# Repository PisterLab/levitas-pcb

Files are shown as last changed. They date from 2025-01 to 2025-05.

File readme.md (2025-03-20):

# LeviTAS PCB

This is a PCB test platform originally built for the LeviTAS project.

A Raspberry Pi Pico microcontroller controls four 0-240V high voltage outputs and can simultaneously read from four FDC2112 capacitance sensors. The architecture and code should be straightforward to re-engineered to add more channels.

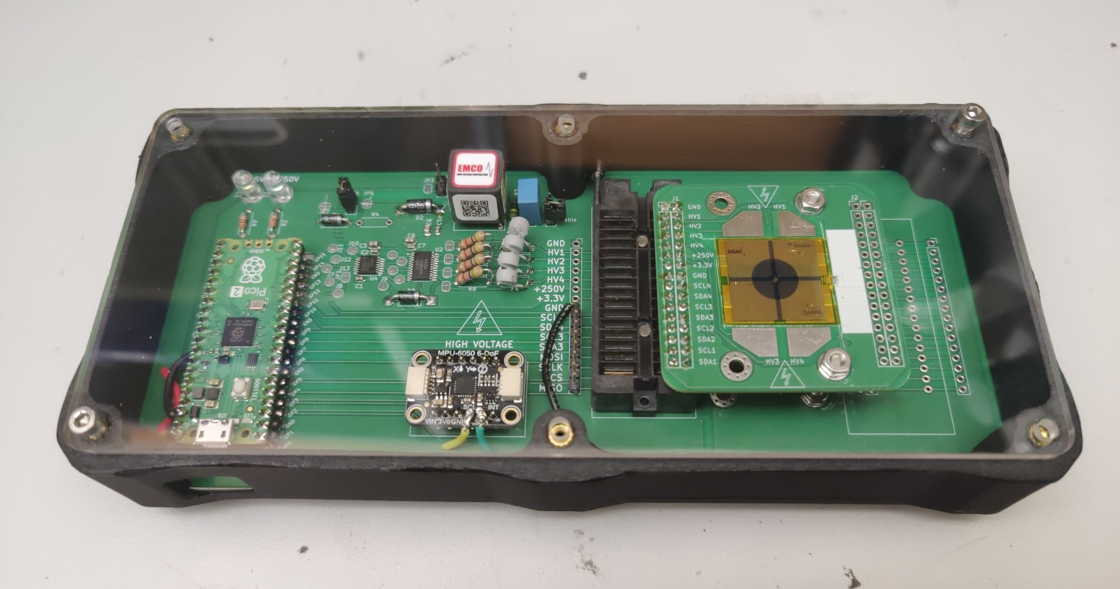
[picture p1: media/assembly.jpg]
Full assembled PCB and enclosure


# Programming / Firmware

This is how to program the microcontroller.

## Introduction

This project uses the Raspberry Pi RP2350 microcontroller, which is mounted to a Raspberry Pi Pico 2 dev board that we solder onto the main project PCB. The dev board is cheap and convenient because in addition to the RP2350 itself it includes flash memory, an oscillator, and power circuitry that we'd otherwise have to include anyway. The programming is the same either way.

The RP2350 is uniquely good for our use case because we need (a) four I2C buses running in parallel to read FDC2112 capacitance sensors, for which we use the PIO modules available only on the RP2040 and RP2350, and (b) we'd like floating-point math support built into the hardware, which the RP2350 has but the RP2040 does not. An FPGA might accomplish roughly the same tasks but is much more expensive and complicated to use.

Programming the RP2350 microcontroller is officially supported in C++ or MicroPython. We use C++ to more easily write programs that satisfy tight timing constraints (e.g., making a control loop as fast as possible). See the Documentation section below for links to the official documentation.

Note we're specifically using the 2.0.0 version of the SDK (because that's what we started with and haven't bothered to update it). Updating this requires updating the pico-sdk subfolder, every mention of the SDK version in other configuration files, and the version of the picotool utility used to upload the software. To minimize compilation issues, we also specifically chose to put the SDK files inside this git repo instead of requiring them to be downloaded to an external directory and linked.

## Installation and Running

Use the following steps to set up a software build environment for the Pico firmware on Linux or Windows, or follow the [official getting started guide](https://datasheets.raspberrypi.com/pico/getting-started-with-pico.pdf) for more generic instructions.

On Linux:
- Install gcc-arm-none-eabi compiler (arm-non-eabi-gcc on nixos)
- Install newlib
- Install cmake and gnumake
- Install picotool
- Install picotool udev rules
- In `firmware` folder, run `make build` to compile code and `make reload` to download and run (or `make` to do both).
- Use your favorite serial monitor to see data the Pico sends over USB.

On Windows:
- Install [Microsoft VS Code](https://code.visualstudio.com/) (This is preferable to VSCodium because the easiest way to read data from the Pico over USB is the Microsoft VS Code Serial Monitor extension, which doesn't work with VSCodium)
- Install the official [Raspberry Pi Pico Visual Studio Code extension](https://marketplace.visualstudio.com/items?itemName=raspberry-pi.raspberry-pi-pico)
- Open the `firmware` folder in VS Code. The Pi Pico extension should automatically detect this as a Pico project, and enable several commands under its quick access menu (click the extension icon on the Activity Bar, then under "Project" should be "Debug Project", "Compile Project", "Run Project (USB)", etc).
- Use the following commands:
  - "Compile Project" will compile (only) the software and put the compiled executables in a `build` subfolder, but note that "Configure CMake" must be run first.
  - "Configure CMake" will create a `build` subfolder and prepare the compilation based on configuration information in the `CMakeLists.txt` file. This is run automatically when the folder is opened in VS Code if recognized by the Pico extension. NOTE: THIS MUST BE MANUALLY RE-RUN EVERY TIME YOU CHANGE `CMakeLists.txt` FOR THE CHANGES TO BE APPLIED!
  - "Run Project (USB)" will load the program onto a Rasberry Pi Pico 2 board connected over USB (specifically, by running the `picotool` command line utility). If the Pico is in BOOTSEL mode (achieved by holding down the BOOTSEL button before plugging in USB) it will probably work immediately. If not, uploading can still work if USB communication was enabled on the already-running Pico program (which it is for this software, as per `CMakeLists.txt`), though you might need to press "Run Project (USB)" twice.
  - "Debug Project" and "Flash Project (SWD)" do not work without use of the Raspberry Pi Debug Probe (which we don't have).
- To see data the Pico is sending over USB, open the "SERIAL MONITOR" tab on the lower VS Code panel that also has "TERMINAL", "DEBUG CONSOLE", etc., set to 115200 baud and the correct COM port. Note this requires `pico_enable_stdio_usb(levitas 1)` to be set in `CMakeLists.txt` and `stdio_init_all();` to be called in `main.c` (which they are).

## Notable Firmware files

Inside the `firmware` folder:

- `CMakeLists.txt` configures compilation, and must be manually changed to include new source code files or other settings (e.g., importing a new sublibrary for the Pico SDK)
- `src/main.c` is the main source code file and holds the main LeviTAS control loop.
  - by default, this only prints capacitive sensor readings over USB; high voltage is set to zero
  - uncomment code in the main loop to enable high voltage output
- `src/pio_i2c.c`, `src/pio_i2c.h`, and `src/pio_i2c.pio` together form a library that can run I2C communication via the Pico PIOs. `src/main.c` uses this library to run four I2C ports in parallel (to connect to four FDC2112 chips).
- the following test code is unused but can be enabled by changing `CMakeLists.txt` to make them the main project file instead of `main.c`:
  - `src/test_fdc2112_i2c.c` tests only two of the four connected FDC2112 chips by using the two hardware built-in I2C modules (instead of PIO)
  - `src/test_fdc2112_pio_i2c.c` tests all four connected FDC2112 chips using the PIO library, and is almost identical to code in `src/main.c`.
  - `src/test_max5715_spi.c` tests the MAX5715 DAC and high voltage output, and is almost identical to code in `src/main.c`.
  - `src/test_mpu6050_i2c.c` displays data the MPU6050 accelerometer on the PCB motherboard using one of the hardware built-in I2C modules.

Other files:
- `Makefile` is used only for compiling on Linux, not for VS Code
- `.vscode` and `pico_sdk_import.cmake` are used only for VS Code with the official Pico VS Code extension, not on Linux
- the `build` subfolder is automatically generated by cmake when compiling and contains compiled executables in several formats, including UF2.

## Data Collection

The `data-collection/collect-data.py` and `data-collection/graph-data.py` Python programs in the `data-collection` subfolder of the main git repo can be used to automatically read the data the microcontroller sends over USB, then graph it. This provides much more useful data than manually looking at the printed output in a serial monitor.

## Some Useful Notes

There are several ways to upload code to a RP2040 or RP2350 chip:
1. Put into BOOTSEL mode (on Pi Pico dev board, hold down BOOTSEL buton when connecting power/USB), at which point the built-in ROM makes it act like a USB mass storage device. Upload file. (To verify file uploaded correctly, use picotool)
2. Put into BOOTSEL mode, use picotool to upload file
3. If USB communication enabled, can use picotool to force exit into BOOTSEL mode (use "picotool load -f" or "-F") then reboot (convenient!). There's no need to press the BOOTSEL button anymore. Note that sometimes this doesn't work on the first try, but repeating the process usually works.
4. Use SWD debugging interface.
Using the BOOTSEL mode (options 1,2) is necessary on a new chip, but afterward, as long as a program with USB communication enabled is running, option 3 is much more convenient. This is what we generally use.

Notes on the C/C++ SDK (from PDF manual):
- Consists of a large number of CMake libraries (in pico-sdk/src/rp2_common), which must be linked in the per-project CMakeLists.txt
  - The default library used in most examples is pico_stdlib, which includes several other libraries
  - the include files are typically in pico-sdk/src/rp2_common/(CMake library name)/include/(pico, hardware, gpio, etc)/(header.h)
- Apparently has some ability to build/debug running on the host operating system instead of the RP2040?
- Definitions for dev boards are in pico-sdk/src-boards/include/boards/
- The PDF manual has a bunch of examples
- Standard stdin/stdout can use (chapter 2.7):
  - UART (easy) (enabled by default) (disable by calling pico_enable_stdio_uart in CMakeLists.txt)
  - a USB CDC ACM virtual serial port (via TinyUSB) (enable by linking pico_stdio_usb or calling pico_enable_stdio_usb in CMakeLists.txt)
        (this is generally my preference?)
  - serial wire debug link (semihosting)
  - Segger RTT
- Can use bi_decl() in C code to store information in compiled binaries that picotool can access (e.g., comments, pin numbers)

## Documentation

There is a large amount of good official documentation at the following links. The most useful documentation is noted.

https://www.raspberrypi.com/documentation/microcontrollers/

RP2350 microcontroller:
- https://www.raspberrypi.com/products/rp2350/
- (good details on RP2350 hardware/capabilities) https://datasheets.raspberrypi.com/rp2350/rp2350-datasheet.pdf
- https://datasheets.raspberrypi.com/rp2350/hardware-design-with-rp2350.pdf
- https://datasheets.raspberrypi.com/rp2350/rp2350-product-brief.pdf

Pico and Pico 2 dev boards (which are almost identical):
- https://datasheets.raspberrypi.com/pico/pico-datasheet.pdf
- (good software getting-started guide) https://datasheets.raspberrypi.com/pico/getting-started-with-pico.pdf

Programming with C/C++:
- https://github.com/raspberrypi/pico-sdk
- (code examples) https://github.com/raspberrypi/pico-examples
- https://www.raspberrypi.com/documentation/microcontrollers/c_sdk.html
- https://www.raspberrypi.com/documentation/pico-sdk/index_doxygen.html
- (good software getting-started guide) https://datasheets.raspberrypi.com/pico/getting-started-with-pico.pdf
- (very thorough reference) https://datasheets.raspberrypi.com/pico/raspberry-pi-pico-c-sdk.pdf

Picotool:
- An official (and open source) CLI tool to work with compiled binaries and communicate with boards when in BOOTSEL mode (using the PICOBOOT interface; see RP2040 datasheet). Used to load and verify programs.
- https://github.com/raspberrypi/picotool

Raspberry Pi Debug Probe:
- Device to use UART or SWD debugging. Optional. We don't have one.
- https://www.raspberrypi.com/products/debug-probe/
- https://www.raspberrypi.com/documentation/microcontrollers/debug-probe.html

# More pictures

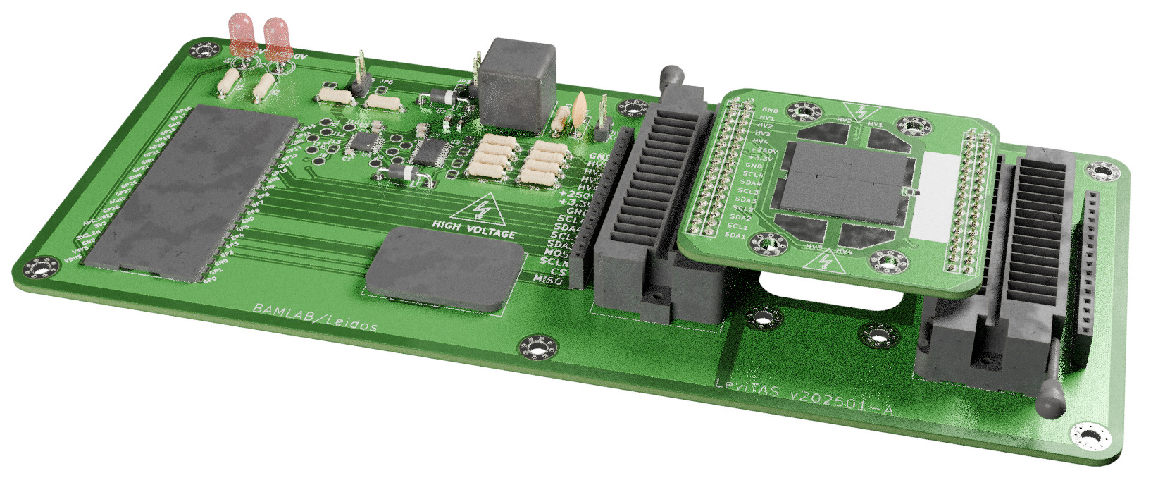
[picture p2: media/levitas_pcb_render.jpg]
Stacked PCBs

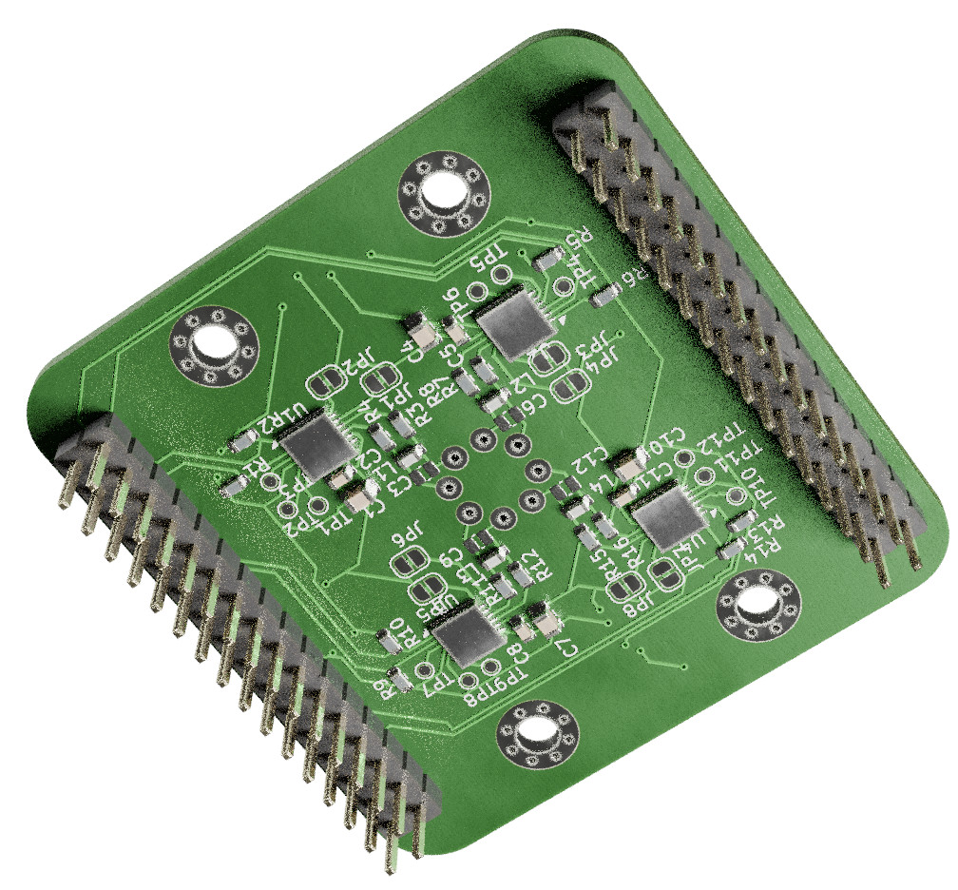
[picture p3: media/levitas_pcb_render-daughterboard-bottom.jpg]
Daughterboard


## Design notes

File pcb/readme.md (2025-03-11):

# Bill of Materials

MOTHERBOARD

|--------------------+-----------+-----------------------------------------+----------+--------------------------|
| TOTAL QTY TO ORDER | PER BOARD | part                                    | COST PER | DigiKey part             |
|--------------------+-----------+-----------------------------------------+----------+--------------------------|
|                  5 |         1 | RP2350 Pico 2 board (SC1631)            | $5       | 2648-SC1631CT-ND         |
|--------------------+-----------+-----------------------------------------+----------+--------------------------|
|                    |         2 | 220ohm R thru-hole                      |          | S220QCT-ND               |
|                    |         1 | LED 5mm thru-hole white                 |          | BL-BZX3V4V-1-B02-ND      |
|                    |         1 | LED 5mm thru-hole red                   |          | 754-WP7113SURCK-ND       |
|--------------------+-----------+-----------------------------------------+----------+--------------------------|
|                    |         4 | 100nF 0603 SMD caps                     |          | 311-1523-1-ND            |
|                    |         3 | 4.7uF 0805 SMD caps                     |          | 1276-1244-1-ND           |
|--------------------+-----------+-----------------------------------------+----------+--------------------------|
|                  5 |         1 | MAX5715AAUD+T DAC                       | $14.6    | 175-MAX5715AAUD+TCT-ND   |
|--------------------+-----------+-----------------------------------------+----------+--------------------------|
|                  5 |         1 | HV264 opamp                             | $7.8     | 150-HV264TS-GCT-ND       |
|                    |         1 | 1N4004 diode thru-hole                  |          | 4878-1N4004CT-ND         |
|--------------------+-----------+-----------------------------------------+----------+--------------------------|
|                    |         4 | 5kohm, thru-hole, 400V                  |          | CF12JT4K70CT-ND          |
|                 12 |         4 | PTC fuse PTCCL05H100SBE                 | $0.99    | BC3368-ND                |
|--------------------+-----------+-----------------------------------------+----------+--------------------------|
|                  0 |         1 | Q025-5C power supply                    |          | -                        |
|                  5 |         1 | TVS diode P6KE6.8A-E3/54                | $0.32    | P6KE6.8A-E3/54GICT-ND    |
|                 10 |         1 | 1Mohm, thru-hole, 400V                  | $0.03    | RNV14FAL1M00             |
|                    |         1 | 10nF, thru-hole, 400V                   |          | 495-75587-1-ND           |
|--------------------+-----------+-----------------------------------------+----------+--------------------------|
|                  3 |         1 | Stemma MPU-6050 accelerometer breakout  | $12.95   | 1528-3886-ND             |
|--------------------+-----------+-----------------------------------------+----------+--------------------------|
|                  6 |         2 | ZIF socket                              | $24.49   | A305-ND                  |
|                    |        10 | jumpers                                 |          |                          |
|                    |         3 | 20x breakaway male header pins          |          | 2057-PH1-20-UA-ND        |
|                    |         3 | 20x female header pins                  |          | S7053-ND                 |
|--------------------+-----------+-----------------------------------------+----------+--------------------------|
|                    |         1 | solder paste?                           |          | 315-NC191AX35T5-ND       |
|                    |         1 | rubber feet?                            |          | 3M156065-ND              |
|--------------------+-----------+-----------------------------------------+----------+--------------------------|
|                    |         8 | 100nF 0603 SMD caps                     |          | 311-1523-1-ND            |
|                    |         8 | 4.7uF 0805 SMD caps                     |          | 1276-1244-1-ND           |
|--------------------+-----------+-----------------------------------------+----------+--------------------------|
|                 15 |         4 | cap sensor FDC2112QDNTRQ1               | $6.59    | 296-44560-1-ND           |
|                    |         8 | resistor SMD 4.7k 0603                  |          | 311-4.7KGRCT-ND          |
|                    |         8 | resistor SMD 470  0603                  |          | A129684CT-ND             |
|                    |         8 | resistor SMD 0  0603 (just in case)     |          | RMCF0603ZT0R00CT-ND      |
|                    |         4 | inductor SMD 18uH 0603 MLF1608C180KTA00 |          | 445-1028-1-ND            |
|                    |         4 | cap SMD 33pF 0603                       |          | 478-KGM15ACG1H330JTCT-ND |
|--------------------+-----------+-----------------------------------------+----------+--------------------------|

Generate PCB gerbers according to
https://www.pcbway.com/blog/help_center/Generate_Gerber_file_from_Kicad.html
- use copper, paste, silkscreen, mask, edge.cuts
- uncheck "use extended x2 format"
- drill file with "minimal header" and "suppress leading zeros"

When ordering:
- remove label option
- extra urgent

# Accelerometer

Attached for board leveling and reference data.

Using breakout board instead of individual chip because I don't trust my soldering for something that small.

Can use either Adafruit Stemma MPU-6050 breakout or Stemma ADXL345 breakout (same board size, slightly more expensive).

# Motherboard/daughterboard connection

We attach the sensor daughterboard with an IC ZIF socket (well, two sockets). We use this instead of standard 0.1" header pins and sockets because inserting or removing header pins takes significant force, which can significantly shake or warp the daughterboard and might break the fragile MEMS devices on top. Ultimately, of course, we want to build a levitation system capable of sustaining high external forces, but our initial prototypes may not immediately reach that goal. That said, the motherboard PCB has footprints such that it can be assembled with standard female header pins instead of ZIF sockets with no other change in functionality.

The specific ZIF sockets se use are 32-6554-11 "CONN IC DIP SOCKET ZIF 32POS GLD" or 32-6554-10 "CONN IC DIP SOCKET ZIF 32POS TIN" from Aries Electronics due to their relatively high availability and robust construction.

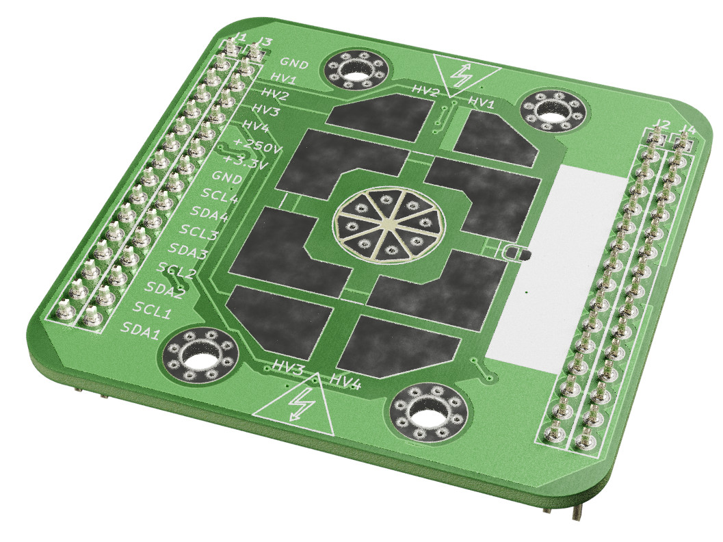
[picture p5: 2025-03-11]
media/levitas_pcb_render-daughterboard-front.jpg

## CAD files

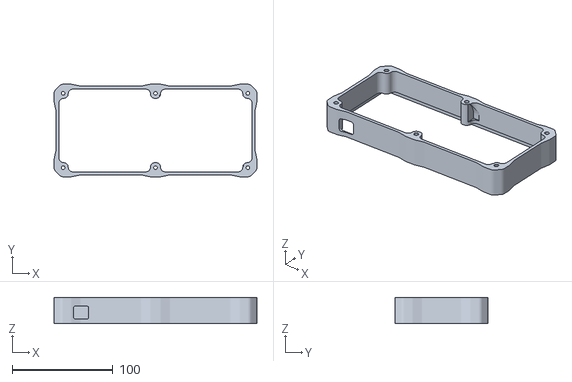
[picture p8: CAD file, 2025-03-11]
enclosure/levitas_pcb_assembly-case.STL
201.0 x 91.8 x 26.0

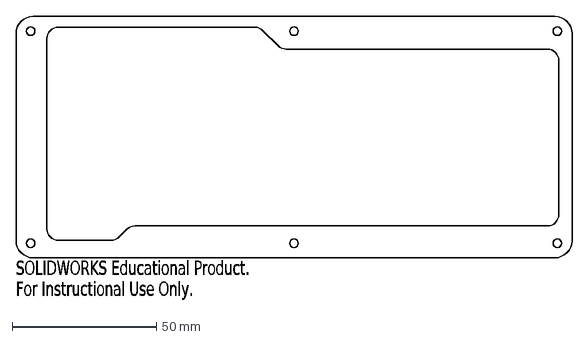
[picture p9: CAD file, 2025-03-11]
enclosure/case_pcb_cover_spacer.DXF
SOLIDWORKS Educational Product.
For Instructional Use Only.

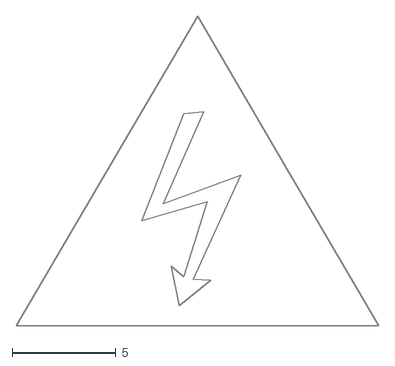
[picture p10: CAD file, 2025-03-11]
pcb/levitas-daughter.v2/high-voltage.dxf
17.5 x 14.9

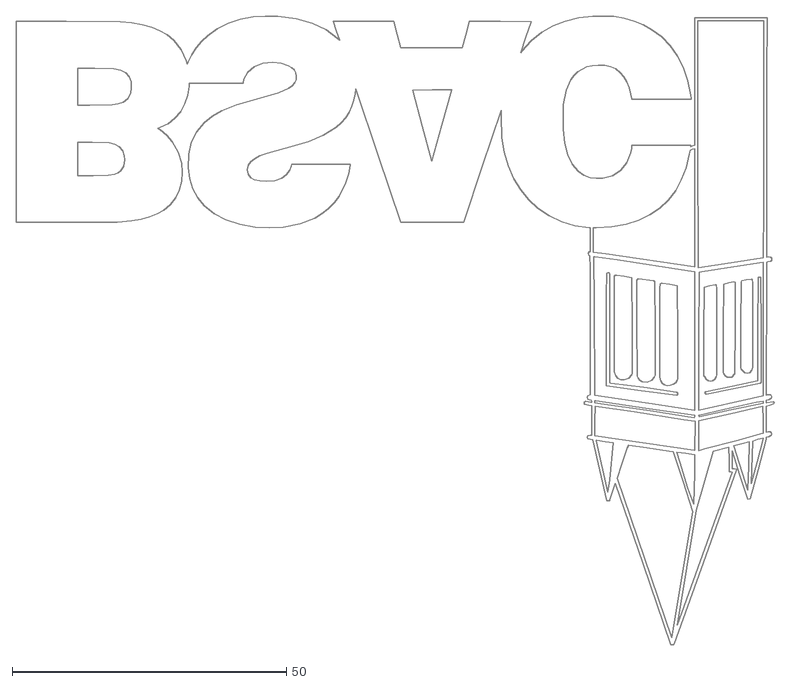
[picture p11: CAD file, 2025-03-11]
pcb/levitas/bsac_logo/BSAC-outline.dxf
138.3 x 114.7

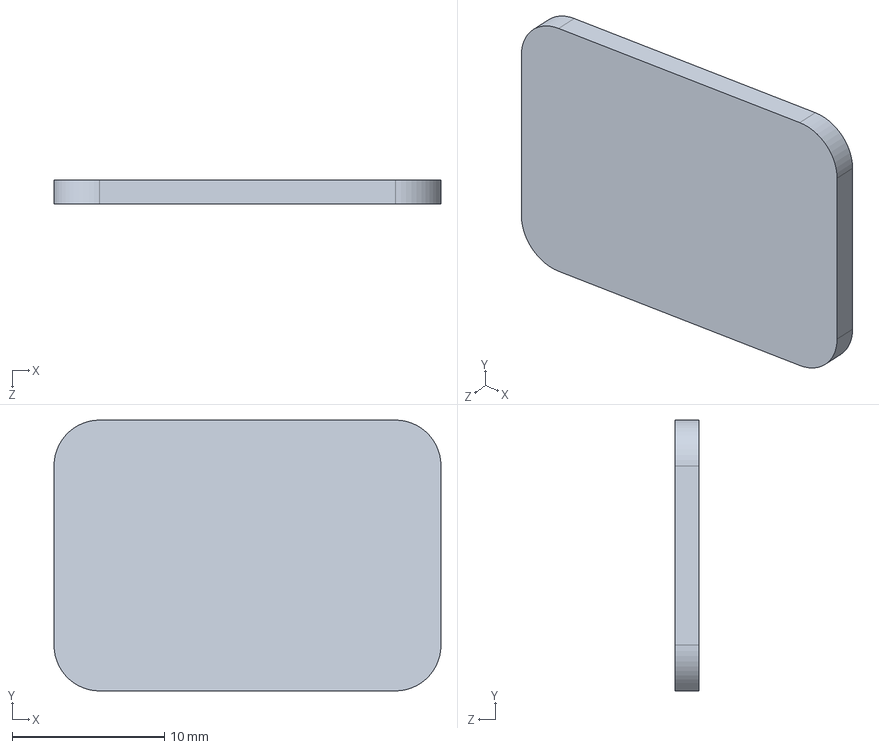
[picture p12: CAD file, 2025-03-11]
pcb/levitas/cad/stemma-mpu-6050.STEP
25.4 x 17.8 x 1.60 mm

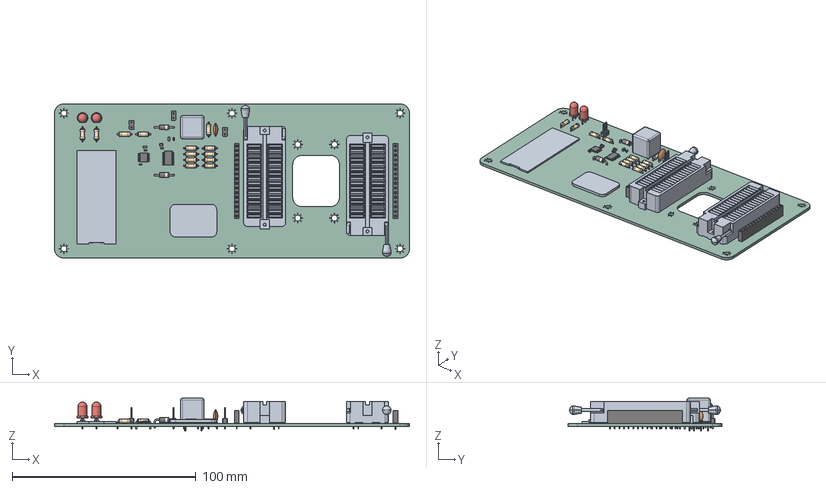
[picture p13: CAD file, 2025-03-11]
pcb/levitas/levitas.step
193.0 x 83.8 x 17.8 mm
R_Axial_DIN0207_L63mm_D25mm_P762mm_Horizontal x 13
PinHeader_1x02_P254mm_Vertical x 3
C_0805_2012Metric x 3
TSSOP_24_44x78mm_P065mm
C_0603_1608Metric x 4
zif-socket x 2
PinSocket_1x16_P254mm_Vertical x 4
stemma-mpu-6050
TSSOP_14_44x5mm_P065mm
LED_D5.0mm x 2
q025-5
pico
D_DO-41_SOD81_P10.16mm_Horizontal x 2
C_Disc_D75mm_W25mm_P500mm
levitas_PCB

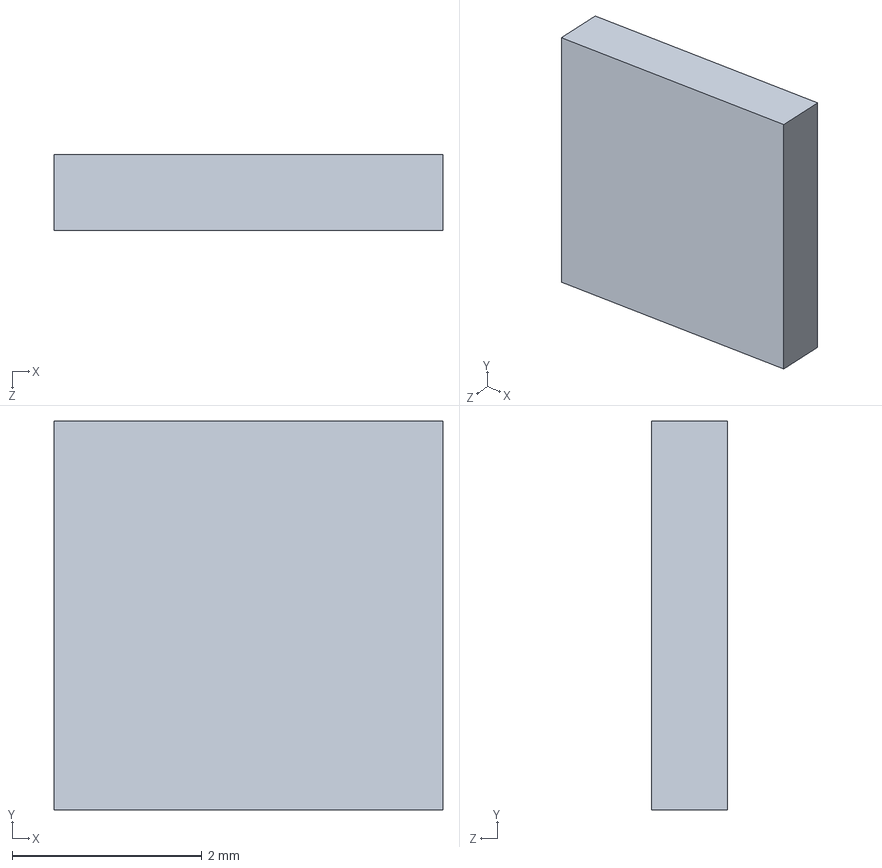
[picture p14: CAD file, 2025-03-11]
pcb/levitas_daughterboard/cad/fdc2112.STEP
4.10 x 4.10 x 0.8 mm

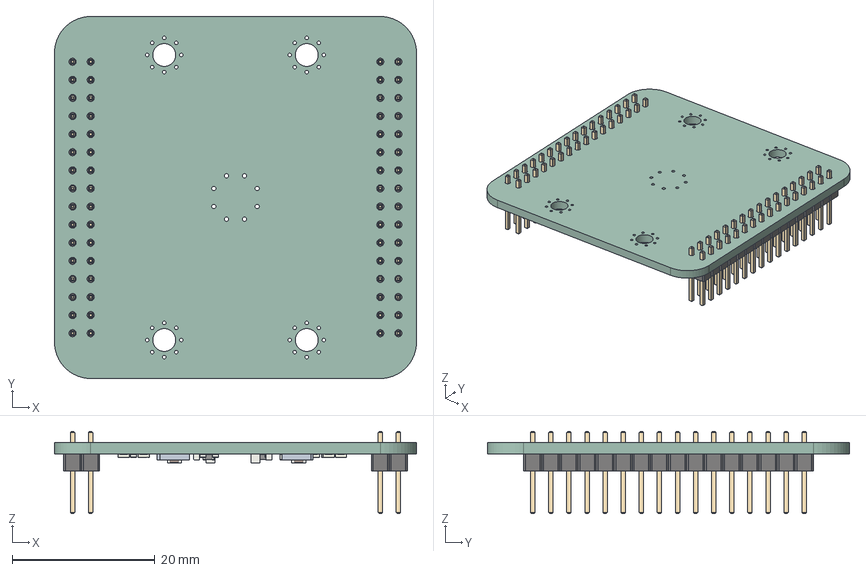
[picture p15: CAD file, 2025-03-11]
pcb/levitas_daughterboard/levitas_daughterboard.step
50.8 x 50.8 x 11.5 mm
PinHeader_1x16_P254mm_Vertical x 4
R_0603_1608Metric x 16
fdc2112 x 4
C_0603_1608Metric x 4
C_0805_2012Metric x 4
L_0603_1608Metric x 4
levitas_daughterboard_PCB

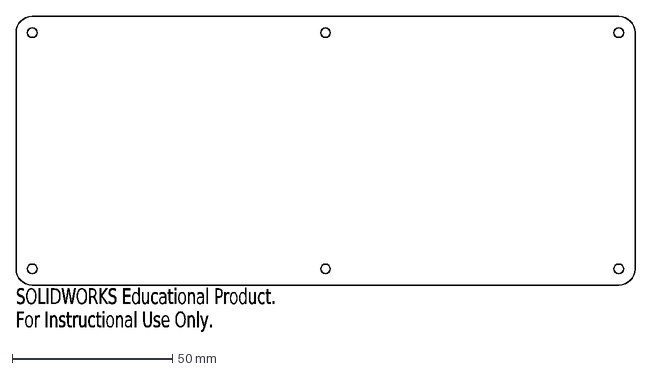
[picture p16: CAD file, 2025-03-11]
enclosure/case_pcb_cover.DXF
SOLIDWORKS Educational Product.
For Instructional Use Only.

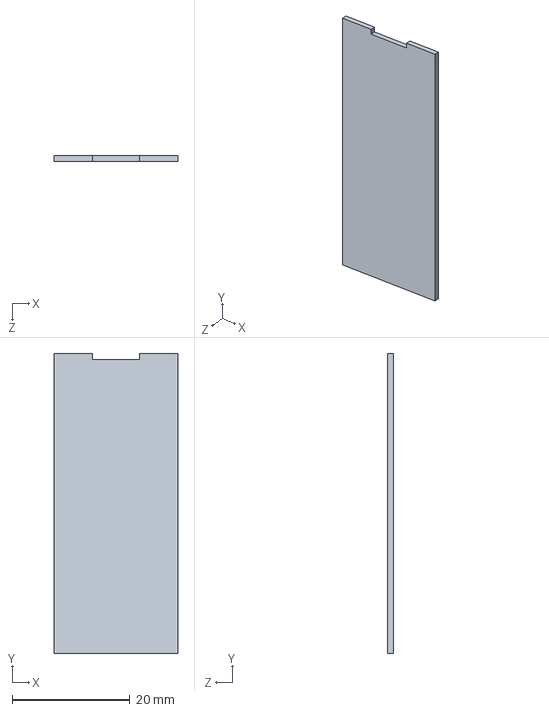
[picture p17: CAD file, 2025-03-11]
pcb/levitas/cad/pico.STEP
21.0 x 51.0 x 1.00 mm

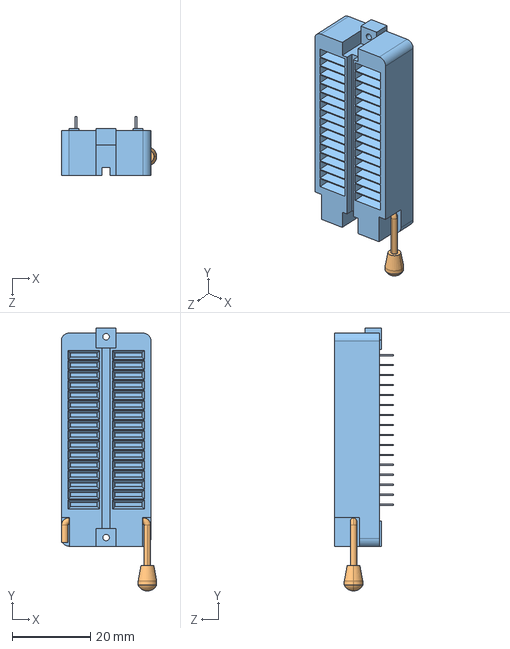
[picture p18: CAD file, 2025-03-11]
pcb/levitas/cad/zif-socket.STEP
24.3 x 67.0 x 14.9 mm

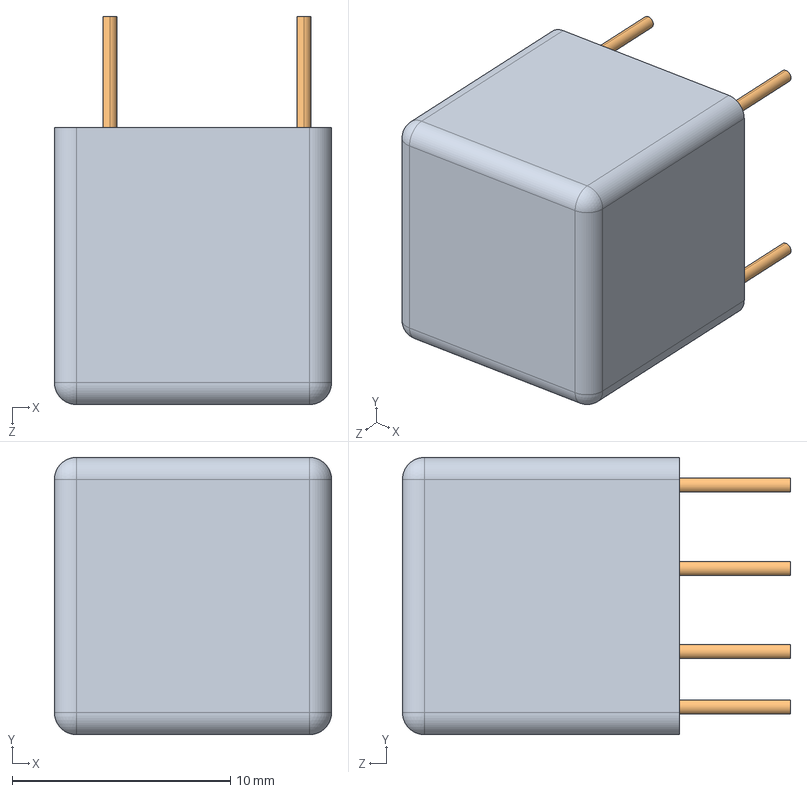
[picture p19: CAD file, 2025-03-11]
pcb/levitas/cad/q025-5.STEP
12.7 x 12.7 x 17.8 mm

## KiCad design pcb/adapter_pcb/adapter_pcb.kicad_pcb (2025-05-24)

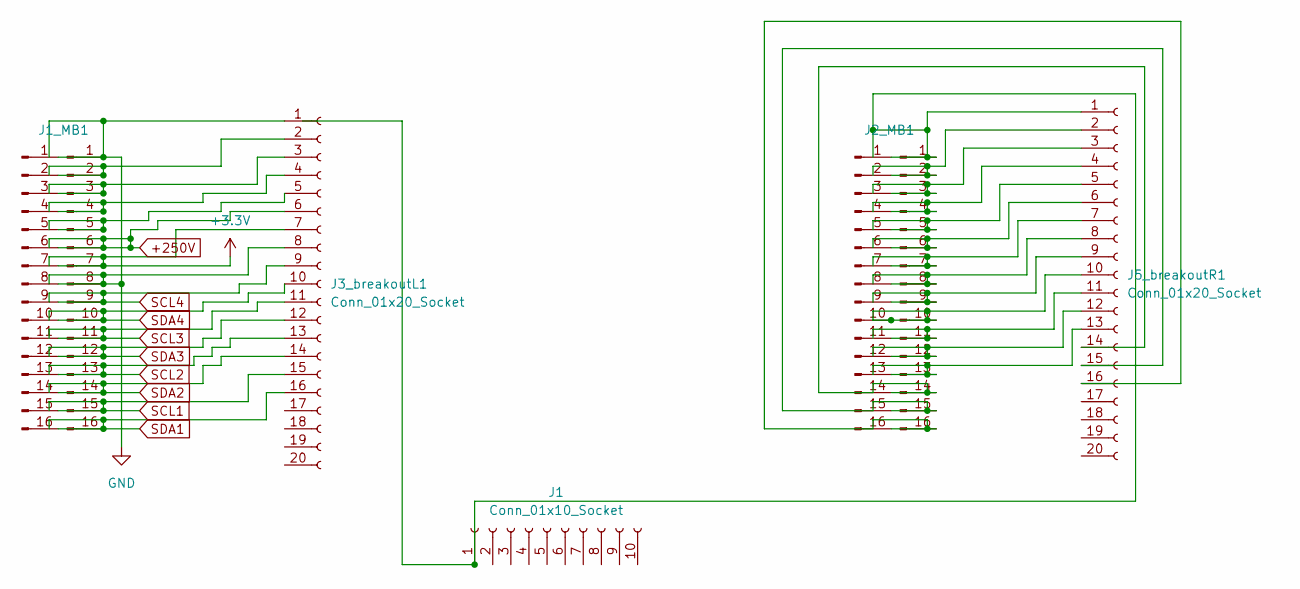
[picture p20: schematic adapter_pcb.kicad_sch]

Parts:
J1: Conn_01x10_Socket; wirebondarray-dteal
J1_MB1, J2_MB1, J3, J5: Conn_01x16_Pin; PinHeader_1x16_P2.54mm_Vertical
J3_breakoutL1, J5_breakoutR1: Conn_01x20_Socket; wirebondarray-1x20-emtan

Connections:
+3.3V: J1_MB1.7, J3.7, J3_breakoutL1.7
+250V: J1_MB1.6, J3.6, J3_breakoutL1.6
unnamed: J1_MB1.2, J3.2, J3_breakoutL1.2
unnamed: J1_MB1.3, J3.3, J3_breakoutL1.3
unnamed: J1_MB1.4, J3.4, J3_breakoutL1.4
unnamed: J1_MB1.5, J3.5, J3_breakoutL1.5
unnamed: J2_MB1.2, J5.2, J5_breakoutR1.2
unnamed: J2_MB1.3, J5.3, J5_breakoutR1.3
unnamed: J2_MB1.4, J5.4, J5_breakoutR1.4
unnamed: J2_MB1.5, J5.5, J5_breakoutR1.5
unnamed: J2_MB1.6, J5.6, J5_breakoutR1.6
unnamed: J2_MB1.7, J5.7, J5_breakoutR1.7
unnamed: J2_MB1.8, J5.8, J5_breakoutR1.8
unnamed: J2_MB1.9, J5.9, J5_breakoutR1.9
unnamed: J2_MB1.10, J5.10, J5_breakoutR1.10
unnamed: J2_MB1.11, J5.11, J5_breakoutR1.11
unnamed: J2_MB1.12, J5.12, J5_breakoutR1.12
unnamed: J2_MB1.13, J5.13, J5_breakoutR1.13
unnamed: J2_MB1.14, J5.14, J5_breakoutR1.14
unnamed: J2_MB1.15, J5.15, J5_breakoutR1.15
unnamed: J2_MB1.16, J5.16, J5_breakoutR1.16
SCL1: J1_MB1.15, J3.15, J3_breakoutL1.15
SCL2: J1_MB1.13, J3.13, J3_breakoutL1.13
SCL3: J1_MB1.11, J3.11, J3_breakoutL1.11
SCL4: J1_MB1.9, J3.9, J3_breakoutL1.9
SDA1: J1_MB1.16, J3.16, J3_breakoutL1.16
SDA2: J1_MB1.14, J3.14, J3_breakoutL1.14
SDA3: J1_MB1.12, J3.12, J3_breakoutL1.12
SDA4: J1_MB1.10, J3.10, J3_breakoutL1.10

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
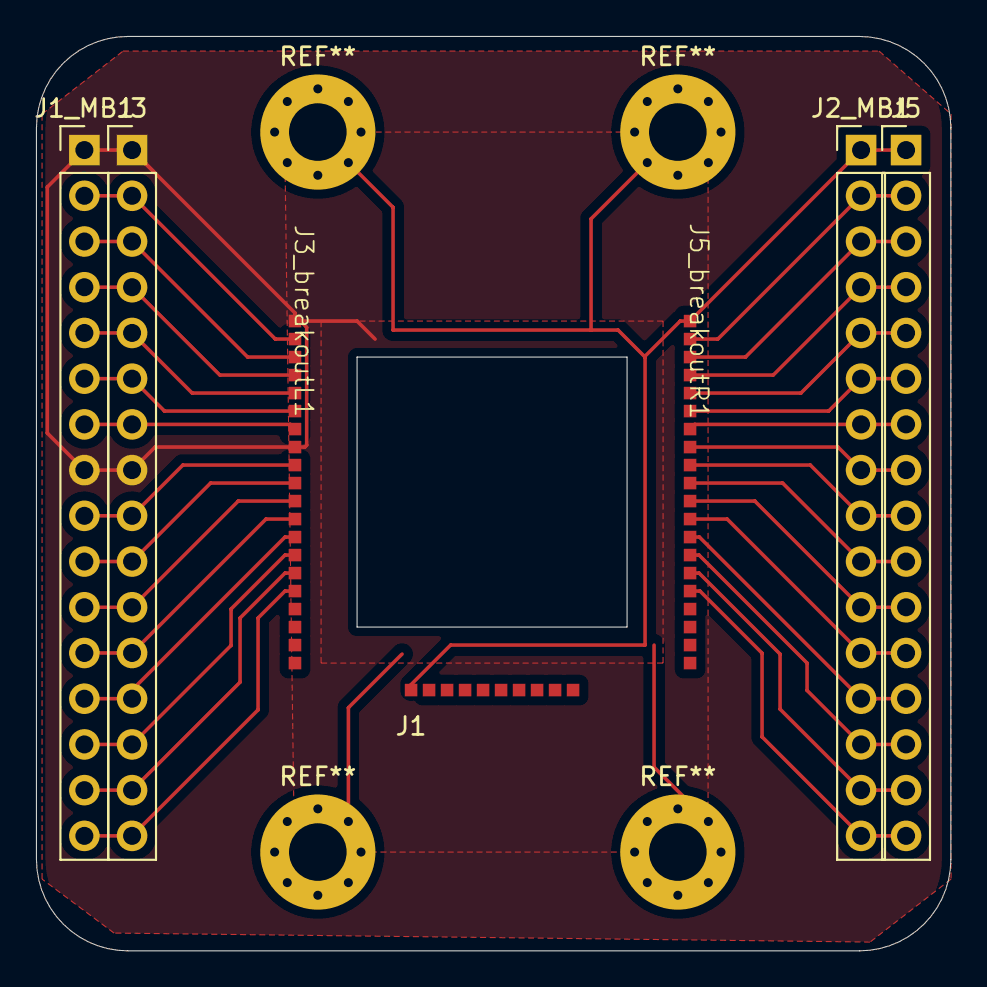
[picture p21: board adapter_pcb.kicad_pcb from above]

Board: 2 copper layers, 50.8 x 50.8 mm, 7 parts (0 on the bottom side), 31 nets.

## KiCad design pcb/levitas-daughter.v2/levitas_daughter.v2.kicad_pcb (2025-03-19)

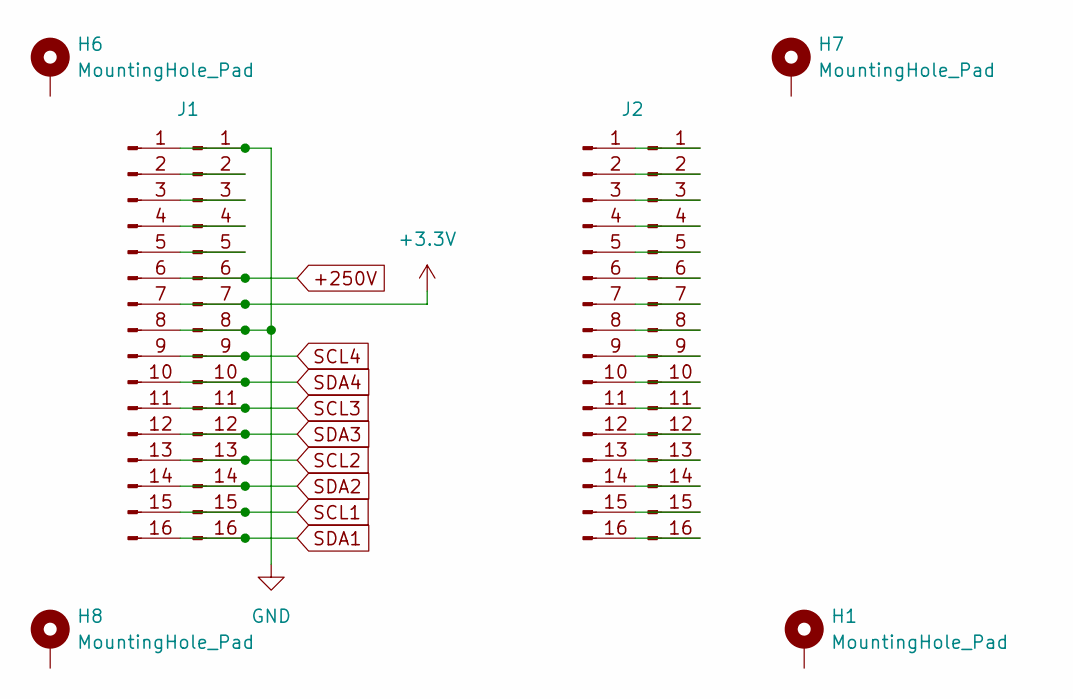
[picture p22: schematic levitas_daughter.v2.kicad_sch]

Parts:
H1, H6, H7, H8: MountingHole_Pad; MountingHole_3.2mm_M3_Pad_Via
J1, J2, J3, J4: Conn_01x16_Pin; PinHeader_1x16_P2.54mm_Vertical

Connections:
+3.3V: J1.7, J3.7
+250V: J1.6, J3.6
GND: J1.1, J1.8, J3.1, J3.8
unnamed: J1.2, J3.2
unnamed: J1.3, J3.3
unnamed: J1.4, J3.4
unnamed: J1.5, J3.5
unnamed: J2.1, J4.1
unnamed: J2.2, J4.2
unnamed: J2.3, J4.3
unnamed: J2.4, J4.4
unnamed: J2.5, J4.5
unnamed: J2.6, J4.6
unnamed: J2.7, J4.7
unnamed: J2.8, J4.8
unnamed: J2.9, J4.9
unnamed: J2.10, J4.10
unnamed: J2.11, J4.11
unnamed: J2.12, J4.12
unnamed: J2.13, J4.13
unnamed: J2.14, J4.14
unnamed: J2.15, J4.15
unnamed: J2.16, J4.16
SCL1: J1.15, J3.15
SCL2: J1.13, J3.13
SCL3: J1.11, J3.11
SCL4: J1.9, J3.9
SDA1: J1.16, J3.16
SDA2: J1.14, J3.14
SDA3: J1.12, J3.12
SDA4: J1.10, J3.10

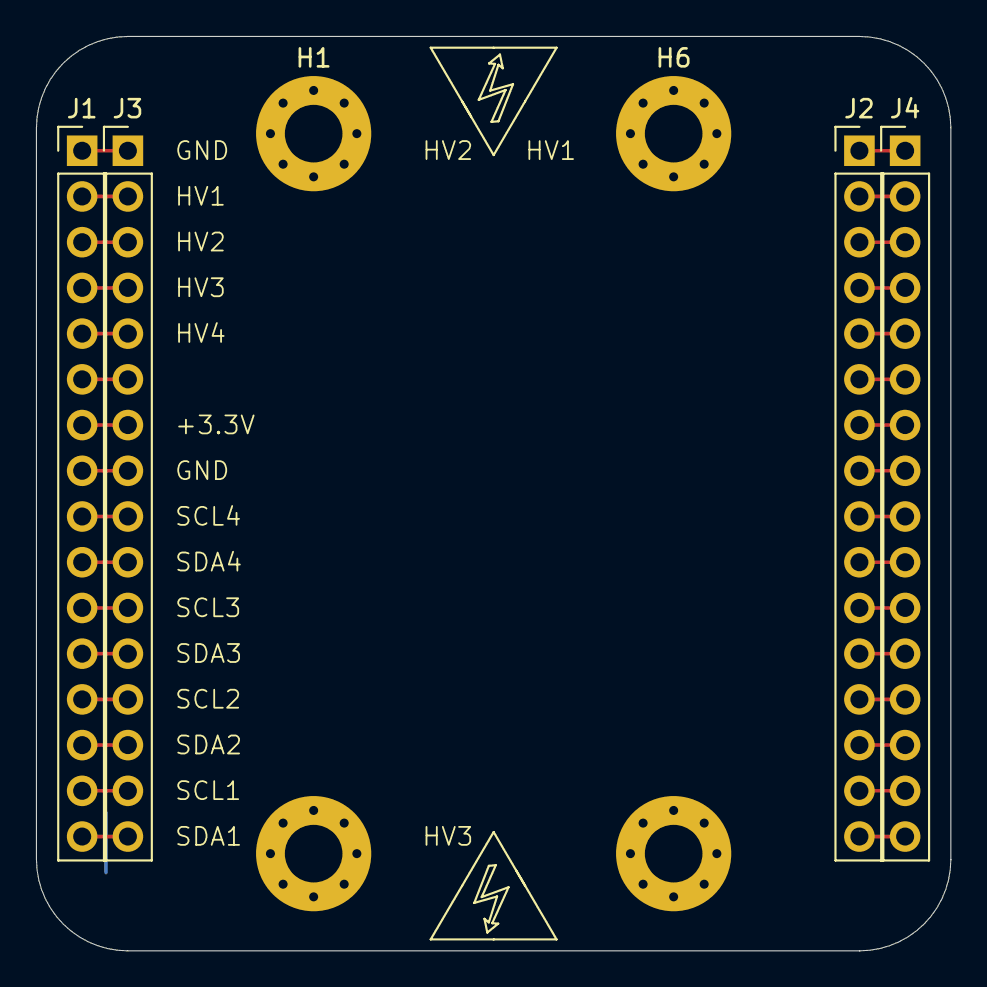
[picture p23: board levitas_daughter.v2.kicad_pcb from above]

Board: 2 copper layers, 50.8 x 50.8 mm, 8 parts (0 on the bottom side), 31 nets.

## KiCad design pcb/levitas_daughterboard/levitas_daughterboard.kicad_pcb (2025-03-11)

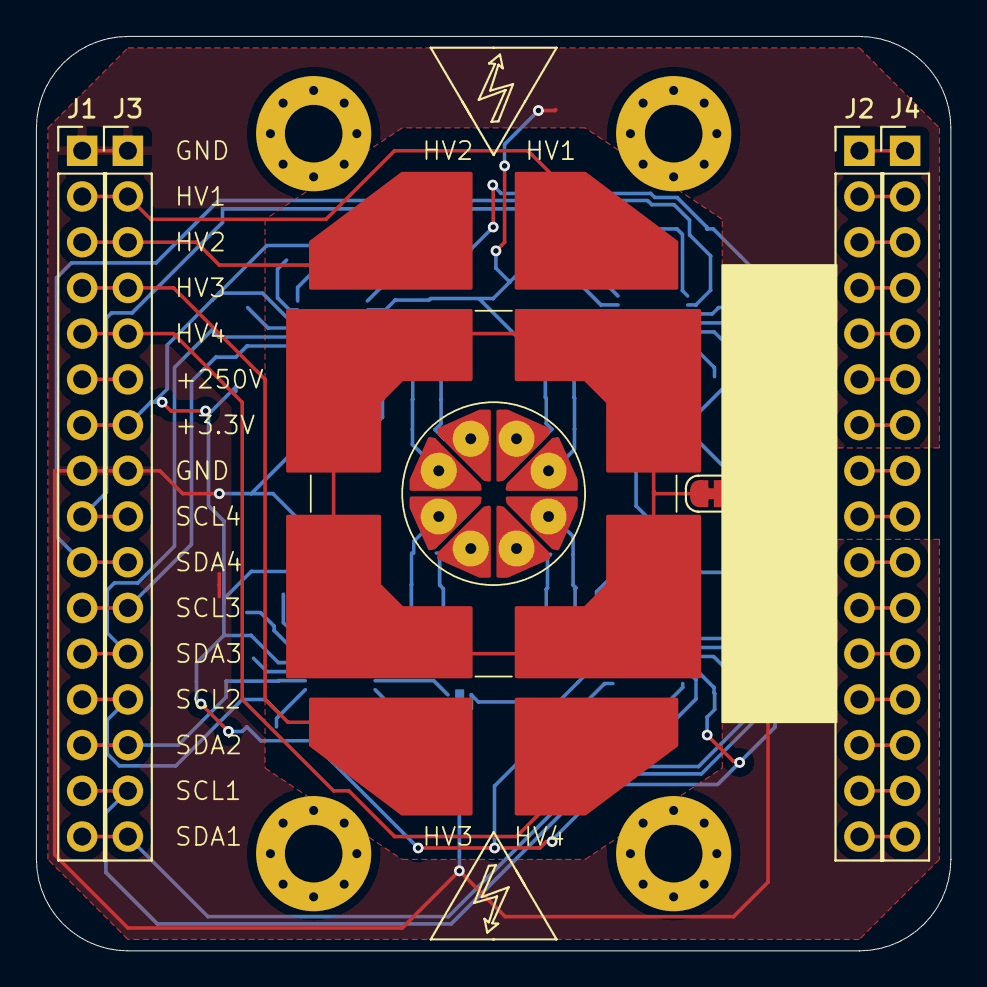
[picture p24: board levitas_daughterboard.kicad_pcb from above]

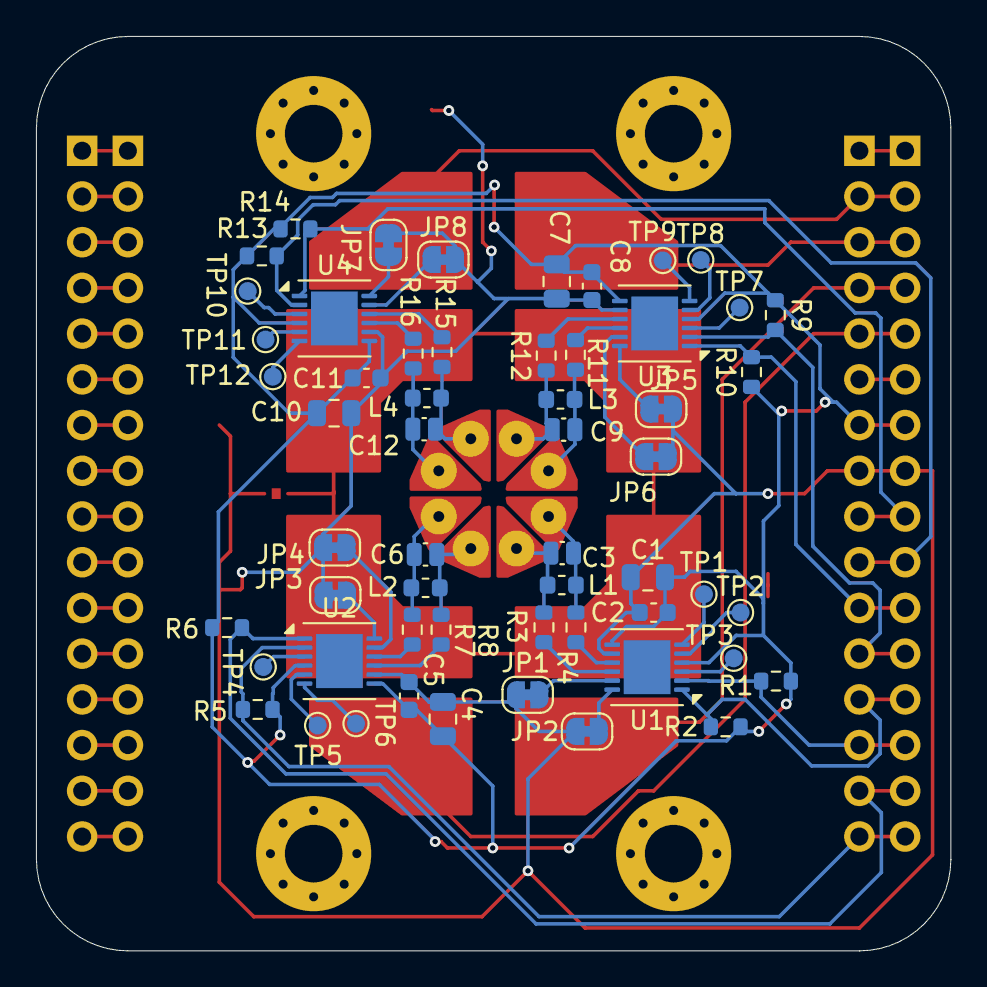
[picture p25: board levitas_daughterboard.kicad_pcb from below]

Board: 2 copper layers, 50.8 x 50.8 mm, 68 parts (62 on the bottom side), 67 nets.

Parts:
C1, C4, C7, C10: 4.7u; C_0805_2012Metric
C2, C5, C8, C11: 100n; C_0603_1608Metric
C3, C6, C9, C12: 33p; C_0504_1310Metric_Pad0.83x1.28mm_HandSolder
J1, J2, J3, J4: Conn_01x16_Pin; PinHeader_1x16_P2.54mm_Vertical
J5, J6, J7, J8, J9, J10, J11, J12: Conn_01x01_Pin; cap_sensor
JP1, JP2, JP3, JP4, JP5, JP6, JP7, JP8: SolderJumper_2_Bridged; SolderJumper-2_P1.3mm_Bridged_RoundedPad1.0x1.5mm
L1, L2, L3, L4: 18u; L_0603_1608Metric
R1, R2, R5, R6, R9, R10, R13, R14: 4.7k; R_0603_1608Metric
R3, R4, R7, R8, R11, R12, R15, R16: 470; R_0603_1608Metric
TP1, TP2, TP3, TP4, TP5, TP6, TP7, TP8, TP9, TP10, TP11, TP12: TestPoint; TestPoint_Pad_D1.0mm
U1, U2, U3, U4: FDC2112; WSON-12-1EP_4x4mm_P0.5mm_EP2.6x3mm

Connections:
+3.3V: C1.1, C2.1, C4.1, C5.1, C7.1, C8.1, C10.1, C11.1, J1.7, J3.7, R1.1, R2.1, R5.1, R6.1, R9.1, R10.1, R13.1, R14.1, U1.4 (ADDR), U1.7 (VDD), U2.4 (ADDR), U2.7 (VDD), U3.4 (ADDR), U3.7 (VDD), U4.4 (ADDR), U4.7 (VDD)
+250V: J1.6, J3.6
GND: C1.2, C2.2, C4.2, C5.2, C7.2, C8.2, C10.2, C11.2, J1.1, J1.8, J3.1, J3.8, JP1.2 (B), JP2.2 (B), JP3.2 (B), JP4.2 (B), JP5.2 (B), JP6.2 (B), JP7.2 (B), JP8.2 (B), U1.8 (GND), U2.8 (GND), U3.8 (GND), U4.8 (GND)
unnamed: J1.2, J3.2
unnamed: J1.3, J3.3
unnamed: J1.4, J3.4
unnamed: J1.5, J3.5
unnamed: J2.1, J4.1
unnamed: J2.2, J4.2
unnamed: J2.3, J4.3
unnamed: J2.4, J4.4
unnamed: J2.5, J4.5
unnamed: J2.6, J4.6
unnamed: J2.7, J4.7
unnamed: J2.8, J4.8
unnamed: J2.9, J4.9
unnamed: J2.10, J4.10
unnamed: J2.11, J4.11
unnamed: J2.12, J4.12
unnamed: J2.13, J4.13
unnamed: J2.14, J4.14
unnamed: J2.15, J4.15
unnamed: J2.16, J4.16
unnamed: C3.1, J5.1, L1.1, R3.1
unnamed: C3.2, J6.1, L1.2, R4.1
unnamed: C6.1, J7.1, L2.1, R7.1
unnamed: C6.2, J8.1, L2.2, R8.1
unnamed: C9.1, J9.1, L3.1, R11.1
unnamed: C9.2, J10.1, L3.2, R12.1
unnamed: C12.1, J11.1, L4.1, R15.1
unnamed: C12.2, J12.1, L4.2, R16.1
unnamed: JP1.1 (A), U1.11 (IN1A)
unnamed: JP2.1 (A), U1.12 (IN1B)
unnamed: JP3.1 (A), U2.12 (IN1B)
unnamed: JP4.1 (A), U2.11 (IN1A)
unnamed: JP5.1 (A), U3.12 (IN1B)
unnamed: JP6.1 (A), U3.11 (IN1A)
unnamed: JP7.1 (A), U4.12 (IN1B)
unnamed: JP8.1 (A), U4.11 (IN1A)
unnamed: TP3.1, U1.3 (CLKIN)
unnamed: R4.2, U1.9 (IN0A)
unnamed: R3.2, U1.10 (IN0B)
unnamed: TP2.1, U1.5 (INTB)
unnamed: TP1.1, U1.6 (SD)
unnamed: TP4.1, U2.3 (CLKIN)
unnamed: R8.2, U2.9 (IN0A)
unnamed: R7.2, U2.10 (IN0B)
unnamed: TP5.1, U2.5 (INTB)
unnamed: TP6.1, U2.6 (SD)
unnamed: TP7.1, U3.3 (CLKIN)
unnamed: R12.2, U3.9 (IN0A)
unnamed: R11.2, U3.10 (IN0B)
unnamed: TP8.1, U3.5 (INTB)
unnamed: TP9.1, U3.6 (SD)
unnamed: TP10.1, U4.3 (CLKIN)
unnamed: R16.2, U4.9 (IN0A)
unnamed: R15.2, U4.10 (IN0B)
unnamed: TP11.1, U4.5 (INTB)
unnamed: TP12.1, U4.6 (SD)
SCL1: J1.15, J3.15, R6.2, U2.1 (SCL)
SCL2: J1.13, J3.13, R2.2, U1.1 (SCL)
SCL3: J1.11, J3.11, R10.2, U3.1 (SCL)
SCL4: J1.9, J3.9, R14.2, U4.1 (SCL)
SDA1: J1.16, J3.16, R5.2, U2.2 (SDA)
SDA2: J1.14, J3.14, R1.2, U1.2 (SDA)
SDA3: J1.12, J3.12, R9.2, U3.2 (SDA)
SDA4: J1.10, J3.10, R13.2, U4.2 (SDA)

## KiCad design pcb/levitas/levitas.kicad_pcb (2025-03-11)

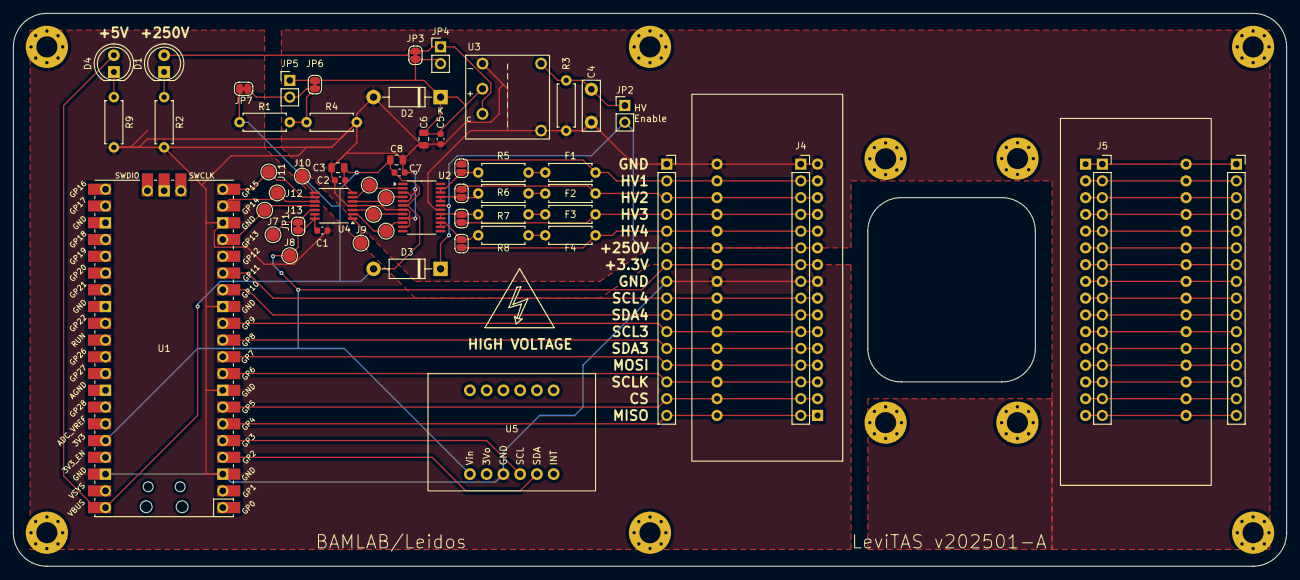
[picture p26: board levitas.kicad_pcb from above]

Board: 2 copper layers, 193.0 x 83.8 mm, 58 parts (0 on the bottom side), 58 nets.

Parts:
C1, C2, C5, C7: 100n; C_0603_1608Metric
C3, C6, C8: 4.7u; C_0805_2012Metric
C4: 10n; C_Disc_D7.5mm_W2.5mm_P5.00mm
D1, D4: LED; LED_D5.0mm
D2: D; D_DO-41_SOD81_P10.16mm_Horizontal
D3: 1N1004; D_DO-41_SOD81_P10.16mm_Horizontal
F1, F2, F3, F4: Polyfuse; R_Axial_DIN0207_L6.3mm_D2.5mm_P7.62mm_Horizontal
J1, J2: zif_socket; ZIF_socket
J3, J4, J5, J6: Conn_01x16_Socket; PinSocket_1x16_P2.54mm_Vertical
J7, J8, J9, J10, J11, J12, J13, J14, J15, J16, J17: Conn_01x01_Pin; TestPoint_Pad_D2.0mm
JP1, JP3, JP6, JP7: SolderJumper_2_Bridged; SolderJumper-2_P1.3mm_Bridged_RoundedPad1.0x1.5mm
JP2: Jumper_2_Bridged; PinHeader_1x02_P2.54mm_Vertical
JP4, JP5: Jumper_2_Open; PinHeader_1x02_P2.54mm_Vertical
JP8, JP9, JP10, JP11: SolderJumper_2_Open; SolderJumper-2_P1.3mm_Open_RoundedPad1.0x1.5mm
R1, R4: R_US; R_Axial_DIN0207_L6.3mm_D2.5mm_P7.62mm_Horizontal
R2, R9: 220; R_Axial_DIN0207_L6.3mm_D2.5mm_P7.62mm_Horizontal
R3: 1M; R_Axial_DIN0207_L6.3mm_D2.5mm_P7.62mm_Horizontal
R5, R6, R7, R8: 5k; R_Axial_DIN0207_L6.3mm_D2.5mm_P7.62mm_Horizontal
U1: Pico; RPi_Pico_SMD_TH
U2: HV264; TSSOP-24_4.4x7.8mm_P0.65mm
U3: Q025-5C
U4: MAX5715; TSSOP-14_4.4x5mm_P0.65mm
U5: MPU-6050 breakout; MPU-6050-breakout

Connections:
+3.3V: C1.1, J1.10, J1.23, J3.7, J4.7, J8.1, JP1.1 (A), U1.36 (3V3), U4.13 (VDDIO), U4.14 (nLDAC), U5.1 (Vin)
+5V: C2.1, C3.1, C7.1, C8.1, D3.2 (A), D4.2 (A), JP7.2 (B), R1.1, U1.40 (VBUS), U2.6 (VDD), U4.7 (VDD)
CS-d: J1.2, J1.31, J3.15, J4.15, U1.7 (GPIO5)
CS-m: J13.1, U1.17 (GPIO13), U4.11 (CSB)
DAC1: J17.1, U2.2 (VIN1), U4.6 (OUTD)
DAC2: J16.1, U2.4 (VIN2), U4.5 (OUTC)
DAC3: J15.1, U2.8 (VIN3), U4.3 (OUTB)
DAC4: J14.1, U2.10 (VIN4), U4.2 (OUTA)
HV1: F1.2, J1.15, J1.18, J3.2, J4.2, JP8.2 (B)
HV2: F2.2, J1.14, J1.19, J3.3, J4.3, JP9.2 (B)
HV3: F3.2, J1.13, J1.20, J3.4, J4.4, JP10.2 (B)
HV4: F4.2, J1.12, J1.21, J3.5, J4.5, JP11.2 (B)
HV+: D3.1 (K), J1.11, J1.22, J3.6, J4.6, JP2.2 (B), U2.19 (VPP)
HV-: C1.2, C2.2, C3.2, C4.2, C5.2, C6.2, C7.2, C8.2, D2.2 (A), J1.9, J1.16, J1.17, J1.24, J3.1, J3.8, J4.1, J4.8, R2.2, R3.2, R4.2, R9.2, U1.3 (GND), U1.8 (GND), U1.13 (GND), U1.18 (GND), U1.38 (GND), U2.3 (RGND1), U2.5 (RGND2), U2.7 (GND), U2.9 (RGND3), U2.11 (RGND4), U2.18 (HVGND), U3.1 (In(-)), U3.4 (HVOut(-)), U4.4 (GND), U5.3 (GND)
MISO-d: J1.1, J1.32, J3.16, J4.16, U1.6 (GPIO4)
MOSI-d: J1.4, J1.29, J3.13, J4.13, U1.10 (GPIO7)
MOSI-m: J11.1, U1.20 (GPIO15), U4.9 (DIN)
unnamed: D1.2 (A), JP3.1 (A), JP4.1 (A), U3.6 (control)
unnamed: D1.1 (K), R2.1
unnamed: C5.1, C6.1, D2.1 (K), JP3.2 (B), JP4.2 (B), JP5.1 (A), JP6.1 (A), U3.2 (In(+))
unnamed: D4.1 (K), R9.1
unnamed: F1.1, R5.2
unnamed: F2.1, R6.2
unnamed: F3.1, R7.2
unnamed: F4.1, R8.2
unnamed: J2.1, J2.32, J5.1, J6.1
unnamed: J2.2, J2.31, J5.2, J6.2
unnamed: J2.3, J2.30, J5.3, J6.3
unnamed: J2.4, J2.29, J5.4, J6.4
unnamed: J2.5, J2.28, J5.5, J6.5
unnamed: J2.6, J2.27, J5.6, J6.6
unnamed: J2.7, J2.26, J5.7, J6.7
unnamed: J2.8, J2.25, J5.8, J6.8
unnamed: J2.9, J2.24, J5.9, J6.9
unnamed: J2.10, J2.23, J5.10, J6.10
unnamed: J2.11, J2.22, J5.11, J6.11
unnamed: J2.12, J2.21, J5.12, J6.12
unnamed: J2.13, J2.20, J5.13, J6.13
unnamed: J2.14, J2.19, J5.14, J6.14
unnamed: J2.15, J2.18, J5.15, J6.15
unnamed: J2.16, J2.17, J5.16, J6.16
unnamed: J7.1, JP1.2 (B), U4.12 (nCLR)
unnamed: J9.1, U4.1 (VREF)
unnamed: J10.1, U4.8 (nRDY)
unnamed: C4.1, JP2.1 (A), R3.1, U3.3 (HVOut(+))
unnamed: JP5.2 (B), JP6.2 (B), JP7.1 (A), R1.2, R4.1
unnamed: JP8.1 (A), R5.1, U2.22 (FB1), U2.23 (VOUT1)
unnamed: JP9.1 (A), R6.1, U2.20 (FB2), U2.21 (VOUT2)
unnamed: JP10.1 (A), R7.1, U2.16 (FB3), U2.17 (VOUT3)
unnamed: JP11.1 (A), R8.1, U2.14 (FB4), U2.15 (VOUT4)
SCL4-d: J1.8, J1.25, J3.9, J4.9, U1.15 (GPIO11)
SCL-d: J1.6, J1.27, J3.11, J4.11, U1.12 (GPIO9)
SCL-m: U1.5 (GPIO3), U5.4 (SCL)
SCLK-d: J1.3, J1.30, J3.14, J4.14, U1.9 (GPIO6)
SCLK-m: J12.1, U1.19 (GPIO14), U4.10 (SCLK)
SDA4-d: J1.7, J1.26, J3.10, J4.10, U1.14 (GPIO10)
SDA-d: J1.5, J1.28, J3.12, J4.12, U1.11 (GPIO8)
SDA-m: U1.4 (GPIO2), U5.5 (SDA)

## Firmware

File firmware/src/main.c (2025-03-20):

// This file is the entry point (and main source code file) for the
// current LeviTAS PCB project.
//
// It contains code to read from four FDC2112 capacitance sensors,
// write voltages to a 4-channel MAX5715 DAC (connected to a HV264
// amplifier), and write data out via a serial port (over USB).

// include necessary standard libraries
#include "pico/stdlib.h"        // standard functions
#include <stdio.h>              // printf
#include "pico/multicore.h"     // send USB printf on second core
#include "pico/util/queue.h"    // queue for multicore communication
#include "pico/time.h"          // assorted time functions
#include "hardware/spi.h"       // SPI for MAX5715
// also include our custom I2C PIO library
#include "pio_i2c.h"

// ===========================================================================
// ===========================================================================
// ========== FDC2112 capacitance sensors ====================================
// ===========================================================================
// ===========================================================================
// (This section contains data and functions to use the capacitance sensors.)
// (adapted from test_fdc2112_pio_i2c.c)

// I2C address of all FDC2112 chips (each on its own I2C bus)
#define FDC2112_I2C_ADDR 0x2b
// I2C-accessible registers of FDC2112 chip
#define FDC2112_REG_DATA_CH0 0x00
#define FDC2112_REG_RCOUNT_CH0 0x08
#define FDC2112_REG_OFFSET_CH0 0x0c
#define FDC2112_REG_SETTLECOUNT_CH0 0x10
#define FDC2112_REG_CLOCK_DIVIDERS_CH0 0x14
#define FDC2112_REG_STATUS 0x18
#define FDC2112_REG_ERROR_CONFIG 0x19
#define FDC2112_REG_CONFIG 0x1a
#define FDC2112_REG_MUX_CONFIG 0x1b
#define FDC2112_REG_RESET_DEV 0x1c
#define FDC2112_REG_DRIVE_CURRENT_CH0 0x1e
#define FDC2112_REG_MANUFACTURER_ID 0x7e
#define FDC2112_REG_DEVICE_ID 0x7f

typedef struct {
    // store four capacitance values
    int16_t data0;
    int16_t data1;
    int16_t data2;
    int16_t data3;
    // store four voltages
    float hv0;
    float hv1;
    float hv2;
    float hv3;
} levitation_state_t;
queue_t data_queue;

// write a 16-bit value to the given register
void fdc2112_write_register(PIO pio, uint sm, uint8_t reg, uint16_t data){
    uint8_t buf[3];
    buf[0] = reg;
    buf[1] = data >> 8; // send MSB byte first
    buf[2] = data & 0xff; // send LSB byte last
    int err = pio_i2c_write_blocking(pio, sm, FDC2112_I2C_ADDR, buf, 3, false);
}
void fdc2112_write_register_4(PIO pio, uint sm0, uint sm1, uint sm2, uint sm3, uint8_t reg, uint16_t data){
    uint8_t buf[3];
    buf[0] = reg;
    buf[1] = data >> 8; // send MSB byte first
    buf[2] = data & 0xff; // send LSB byte last
    pio_i2c_write_blocking_4(pio, sm0, sm1, sm2, sm3, FDC2112_I2C_ADDR, buf, 3, false);
}

// read a 16-bit value from given register
uint16_t fdc2112_read_register(PIO pio, uint sm, uint8_t reg){
    uint8_t buf_reg[1];
    buf_reg[0] = reg;
    uint8_t buf_data[] = {0x00, 0x00};
    pio_i2c_write_blocking(pio, sm, FDC2112_I2C_ADDR, buf_reg, 1, true); // shouldn't stop
    pio_i2c_read_blocking(pio, sm, FDC2112_I2C_ADDR, buf_data, 2);
    // result is MSB then LSB byte
    return (((uint16_t)buf_data[0]) << 8) | ((uint16_t)buf_data[1]);
}
void fdc2112_read_register_4(PIO pio, uint sm0, uint sm1, uint sm2, uint sm3, uint8_t reg, uint16_t* result){
    uint8_t buf_reg[1];
    buf_reg[0] = reg;
    uint8_t buf_data0[] = {0x00, 0x00};
    uint8_t buf_data1[] = {0x00, 0x00};
    uint8_t buf_data2[] = {0x00, 0x00};
    uint8_t buf_data3[] = {0x00, 0x00};
    pio_i2c_write_blocking_4(pio, sm0, sm1, sm2, sm3, FDC2112_I2C_ADDR, buf_reg, 1, true); // shouldn't stop
    pio_i2c_read_blocking_4(pio, sm0, sm1, sm2, sm3, FDC2112_I2C_ADDR, buf_data0, buf_data1, buf_data2, buf_data3, 2);
    // result is MSB then LSB byte
    result[0] =  (((uint16_t)buf_data0[0]) << 8) | ((uint16_t)buf_data0[1]);
    result[1] =  (((uint16_t)buf_data1[0]) << 8) | ((uint16_t)buf_data1[1]);
    result[2] =  (((uint16_t)buf_data2[0]) << 8) | ((uint16_t)buf_data2[1]);
    result[3] =  (((uint16_t)buf_data3[0]) << 8) | ((uint16_t)buf_data3[1]);
}

// read a 16-bit value (assuming register was previously indicated, e.g., by a full read)
uint16_t fdc2112_read_register_nowrite(PIO pio, uint sm){
    uint8_t buf_data[] = {0x00, 0x00};
    //pio_i2c_write_blocking(pio, sm, FDC2112_I2C_ADDR, buf_reg, 1, true); // shouldn't stop
    pio_i2c_read_blocking(pio, sm, FDC2112_I2C_ADDR, buf_data, 2);
    // result is MSB then LSB byte
    return (((uint16_t)buf_data[0]) << 8) | ((uint16_t)buf_data[1]);
}
void fdc2112_read_register_nowrite_4(PIO pio, uint sm0, uint sm1, uint sm2, uint sm3, uint16_t* result){
    uint8_t buf_data0[] = {0x00, 0x00};
    uint8_t buf_data1[] = {0x00, 0x00};
    uint8_t buf_data2[] = {0x00, 0x00};
    uint8_t buf_data3[] = {0x00, 0x00};
    pio_i2c_read_blocking_4(pio, sm0, sm1, sm2, sm3, FDC2112_I2C_ADDR, buf_data0, buf_data1, buf_data2, buf_data3, 2);
    // result is MSB then LSB byte
    result[0] =  (((uint16_t)buf_data0[0]) << 8) | ((uint16_t)buf_data0[1]);
    result[1] =  (((uint16_t)buf_data1[0]) << 8) | ((uint16_t)buf_data1[1]);
    result[2] =  (((uint16_t)buf_data2[0]) << 8) | ((uint16_t)buf_data2[1]);
    result[3] =  (((uint16_t)buf_data3[0]) << 8) | ((uint16_t)buf_data3[1]);
}

static void fdc2112_startup(PIO pio, uint sm){
    // Chip is in sleep state by default and must be enabled.
    // To do so, set a bit in the CONFIG register. First, set the
    // rest of the configuration while we're at it.

    // ===== Measurement time behavior =====
    //
    // First we set the RCOUNT and SETTLECOUNT registers.
    // These control how long the chip takes to read a given signal
    // (see manual pages 15, 16).
    //
    // If the chip is used to read capacitance from multiple channels,
    // SETTLECOUNT determines the amount of time a measurement is
    // allowed to stabilize after switching channels. This does not
    // apply to us, so we set SETTLECOUNT and otherwise ignore it.
    // (TODO CONFIRM THIS WORKS)
    //
    // The chip takes a configurable amount of time to take a measurement.
    // Longer measurement times give more accurate values. The time is
    // determined by RCOUNT (specifically, (RCOUNT*16+4)/f_{REF0} where
    // f_{REF0} is the reference oscillator frequency, about 40MHz).
    // Measuring n bits of precision requires 2^n = (RCOUNT*16).
    // In our case, we want to take measurements within maybe 10us. We
    // choose RCOUNT=33=0x0021 giving 9.04 bits of precision in 13.us.
    // (Note the minimum is RCOUNT>8, which we satisfy; see page 13)
    //
    // (but register map on page 25 says min is 0x0100 or 0x0080?)
    //fdc2112_write_register(pio, sm, FDC2112_REG_RCOUNT_CH0, 0x0040);
    fdc2112_write_register(pio, sm, FDC2112_REG_RCOUNT_CH0, 0x0021);
    // determines the sensor activation time
    // must have settlecount > 3
    fdc2112_write_register(pio, sm, FDC2112_REG_SETTLECOUNT_CH0, 0x000a);

    // ===== Small things =====
    //
    // The chip has some error reporting functions; leave them off
    fdc2112_write_register(pio, sm, FDC2112_REG_ERROR_CONFIG, 0x0000);
    //
    // Prepare to only read capacitance from a single channel on the chip
    // (this setting can choose to alternate readings between channels)
    // 0000 0010 0000 1101 = 0x020d
    fdc2112_write_register(pio, sm, FDC2112_REG_MUX_CONFIG, 0x020d);

    // ===== Gain and offset settings =====
    //
    // The following clock divider setting changes some measurement
    // parameters:
    // f_{REF0}=f_{CLK}/CH0_FREQ_DIVIDER
    // f_{IN0}=f_{SENSOR0}/CH0_FIN_SEL
    fdc2112_write_register(pio, sm, FDC2112_REG_CLOCK_DIVIDERS_CH0, 0x2002);
    //
    // ...and the resulting digital data is 16 bits, of which only
    // 12 bits can be read over I2C. However, the data can be
    // bit-shifted and/or given an offset before I2C reading in order
    // to see the LSB (e.g., if there is only a small capacitance
    // change in a relatively large capacitance).
    //
    // set gain to a 4-bit shift (2^4=16x multiplier):
    // (see manual page 35)
    // 0 0000 00 0 | 0000 0000
    //fdc2112_write_register(pio, sm, FDC2112_REG_RESET_DEV, 0x0000); // 0-bit shift
    //fdc2112_write_register(pio, sm, FDC2112_REG_RESET_DEV, 0x0400); // 3-bit shift
    fdc2112_write_register(pio, sm, FDC2112_REG_RESET_DEV, 0x0600); // 4-bit shift
    //
    // offset:
    // also add an offset value in order to fit data within the bits that we're sending back
    // (see manual page 27)
    //fdc2112_write_register(pio, sm, FDC2112_REG_OFFSET_CH0, 0x0000); // no offset
    fdc2112_write_register(pio, sm, FDC2112_REG_OFFSET_CH0, 0x1800); // set offset=0x1800

    // ===== Drive current =====
    //
    // The current the sensor uses to read capacitance can be adjusted.
    // This results in slightly different capacitance readings.
    // Supposedly there's an optimum value that can be found by tweaking
    // until the sensor output drive signal is about 1.8V, but I wasn't
    // able to measureme of the signal (probably too high frequency?).
    //
    // Using the default values (0x0000) seems to work fine.
    //
    // Determines the drive current:
    // (see chart on manual page 36)
    //
    // code  resulting capacitance readings
    // ====================================
    // 00000 0x01b8 0x01d3 0x01d3 0x01c9
    // 00001 0x01ba 0x01d5 0x01d5 0x01cb
    // 00010 0x01bb 0x01d7 0x01d7 0x01cc
    // 00011 0x01bd 0x01d9 0x01d9 0x01cd
    // ...
    // 01001 0x01c3 0x01df 0x01df 0x01d4
    //
    // Result: higher current -> slightly higher reading?
    // (TBD: measure voltage)
    fdc2112_write_register(pio, sm, FDC2112_REG_DRIVE_CURRENT_CH0, 0x0000);

    // ===== Start measurement =====
    //
    // Upon startup, the chip is in a sleep state. Use the following command
    // to start the chip so we can read capacitance. Note that afterward,
    // additional configuration changes might not work until the chip is
    // powered off and on again (which is why we do this last).
    //
    // At the same time, this register also choose which oscillator to use.
    // We will use the chip's internal oscillator (we don't have an external
    // oscillator connected).
    //
    // Set register 0x1a to 00010100 00000001 = 0x1401
    // (sense on channel 0, no sleep mode, full current, internal oscillator)
    // - this also tells the chip to use its internal reference oscillator
    //   - f_{CLK} = f_{INTCLK}
    //   - f_{INTCLK} = internal clock = 43MHz (approximately; ranges 35-55MHz with manufacturing)
    fdc2112_write_register(pio, sm, FDC2112_REG_CONFIG, 0x1401);
}

// ===========================================================================
// ===========================================================================
// ========== MAX5715 DAC ====================================================
// ===========================================================================
// ===========================================================================
// (This section contains data and functions to use the high voltage output.)
// (adapted from test_max5715_spi.c)

// SPI1 CS is GPIO 13 = Pico pin 17
// SPI1 SCLK is GPIO 14 = Pico pin 19
// SPI1 MOSI is GPIO 15 = Pico pin 20
// SPI1 MISO is not used
#define HVAWG_CS_PIN 13
#define HVAWG_SCLK_PIN 14
#define HVAWG_MOSI_PIN 15

// Sending data to DAC requires sending
// this HVAWG_init_command followed by 3 bytes = 24 bits via SPI.
static inline void HVAWG_init_command(){
    // To start command, raise CS for >= 20ns, then lower
    gpio_put(HVAWG_CS_PIN, 1);
    asm volatile("nop \n nop \n nop \n nop"); // assume <= 150MHz clock
    gpio_put(HVAWG_CS_PIN, 0);
}
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

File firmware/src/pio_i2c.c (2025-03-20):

/**
 * Part of a library to run I2C master from a PIO state machine.
 * (use with pio_i2c.h and pio_i2c.pio)
 *
 * Originally from (then heavily tweaked and commented)
 * https://github.com/raspberrypi/pico-examples/tree/master/pio/i2c
 * Copyright (c) 2021 Raspberry Pi (Trading) Ltd.
 * SPDX-License-Identifier: BSD-3-Clause
 */

#include <stdio.h>
#include "pio_i2c.h"

// bit indices of assorted parts of instruction
// (see PIO program)
const int PIO_I2C_ICOUNT_LSB = 10;
const int PIO_I2C_FINAL_LSB  = 9;
const int PIO_I2C_DATA_LSB   = 1;
const int PIO_I2C_NAK_LSB    = 0;

// determine whether state machine interrupt was set
// (will happen if unexpected NAK was observed)
bool pio_i2c_check_error(PIO pio, uint sm) {
    return pio_interrupt_get(pio, sm);
}

// manually restart state machine after NAK-triggered interrupt
void pio_i2c_resume_after_error(PIO pio, uint sm) {
    // empty FIFO buffer
    pio_sm_drain_tx_fifo(pio, sm);
    // restart by manually making state machine execute an unconditional jump
    // to the desired entry point (beginning of wrap loop)
    pio_sm_exec(pio, sm, (pio->sm[sm].execctrl & PIO_SM0_EXECCTRL_WRAP_BOTTOM_BITS) >> PIO_SM0_EXECCTRL_WRAP_BOTTOM_LSB);
    // clear interrupt
    pio_interrupt_clear(pio, sm);
}

// Put a 16-bin instruction into the PIO state machine FIFO
// (which holds 4 instructions). Nonblocking. Don't check if FIFO is full
// or whether state machine is currently stalled due to I2C ACK error. If
// either is the case, might overwrite data in TX FIFO.
// (basically identical to pio_sm_put() but 16 bits)
static inline void pio_i2c_put16_nocheck(PIO pio, uint sm, uint16_t data) {
    // some versions of GCC dislike this
#ifdef __GNUC__
#pragma GCC diagnostic push
#pragma GCC diagnostic ignored "-Wstrict-aliasing"
#endif
    *(io_rw_16 *)&pio->txf[sm] = data;
#ifdef __GNUC__
#pragma GCC diagnostic pop
#endif
}

// Same as pio_i2c_put16_nocheck(), but blocks until TX FIFO has room,
// and also errors out on I2C NAK issues.
void pio_i2c_put16_or_err(PIO pio, uint sm, uint16_t data) {
    // block while state machine FIFO is full
    while (pio_sm_is_tx_fifo_full(pio, sm))
        if (pio_i2c_check_error(pio, sm))
            return;
    if (pio_i2c_check_error(pio, sm))
        return;
    // some versions of GCC dislike this
#ifdef __GNUC__
#pragma GCC diagnostic push
#pragma GCC diagnostic ignored "-Wstrict-aliasing"
#endif
    *(io_rw_16 *)&pio->txf[sm] = data;
#ifdef __GNUC__
#pragma GCC diagnostic pop
#endif
}

// Get data from FIFO.
// Although the state machine hardware returns 16 bits,
// only 8 of them are meaningful: these are the bits
// from the I2C bus. The others should be zero.
uint8_t pio_i2c_get(PIO pio, uint sm) {
    return (uint8_t)pio_sm_get(pio, sm);
}
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

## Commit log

2025-01-27 Serial print demo for 20250123 assembled board
2025-01-28 Enable Pico board 3.3V bus PWM mode for low noise
2025-02-10 FDC2112 capacitive sensor I2C working
2025-02-12 Two FDC2112 sensors working simultaneously
2025-02-28 Moved USB printf to second core
2025-02-28 Multicore printing with low frequency drift
2025-03-10 Capacitor sensor readout and plotting working
2025-03-10 Combine capacitance sensing and high voltage
2025-03-11 Add PCB files
    [BSAC-outline.dxf, fdc2112.STEP, high-voltage.dxf, levitas-B_Cu.gbr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]
2025-03-11 Add enclosure files
    [case_pcb_cover.DXF, case_pcb_cover_spacer.DXF, levitas_pcb_assembly-case.STL]
2025-03-11 Update PCB files to KiCad 9
    [levitas.kicad_sch, levitas_daughterboard.kicad_sch]
2025-03-18 This is the daughter board version 2 with no capacitance sensors
    [high-voltage.dxf, levitas_daughter.v2.kicad_pcb, levitas_daughter.v2.kicad_sch]
2025-03-18 This is the design for the daughter board without capacitance sensors
    [levitas_daughter.v2.kicad_pcb]
2025-03-19 v2 without copper layer, without capacitance sensors
    [levitas_daughter.v2.kicad_pcb]
2025-03-20 Add high voltage code and extra commentary
2025-04-15 adapter pcb to connect MEMS breakout board to motherboard
    [adapter_pcb.kicad_pcb, adapter_pcb.kicad_sch]
2025-05-24 updated adapter-pcb + gerber zip files(need yichen to review)
    [adapter_pcb-B_Cu.gbr, adapter_pcb-B_Mask.gbr, adapter_pcb-B_Paste.gbr, adapter_pcb-B_Silkscreen.gbr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]
